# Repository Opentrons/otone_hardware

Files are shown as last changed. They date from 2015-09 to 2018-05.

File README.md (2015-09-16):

# OT.One Hardware

This repository contains all 3D models and Bill of Materials necessary for independent construction of the opensource OT.One lab automation platform.

If you require more information or assets to complete your construction, please don't hesitate to create an issue in this repository.

This hardware is meant to operate in conjunction with an integrated [software stack](https://github.com/OpenTrons/otone_central), designed for the Raspberry Pi.

## Open Parts List

### Lasercut

* 1001 - [Baseplate](models/1001_A_Baseplate.dxf) x1 (6061 Aluminum, Anodized, 3mm)
* 1002 - [Motor Mount Plate](models/1002_Motor_Mount_Plate.dxf) x5 (6061 Aluminum, Anodized, 3mm)
* 1003 - Computer Mount Set x1 (Acrylic, 3mm)
* 1004 - [Home Switch Mount Set](models/1004_Home_Switch_Mount_Set.dxf) x1 (Acrylic, 3mm)
* 1005 - [Z Rail Spacer](models/1005_Z_Rail_Spacer.dxf) x1 (Acrylic, 5mm)
* 1006 - [Pipette Rail Mount](models/1006_Pipette_Rail_Mount.dxf) x1 (Acrylic, 5mm)
* 1007 - [A Motor Mount Set](models/1007_A_Motor Mount_Set.dxf) x1 (Acrylic, 8mm)
* 1008 - [Z Motor Mount](models/1008_Z_Motor_Mount.dxf) x1 (Acrylic, 8mm)
* 1009 - [Z Motor Lock](models/1009_Z_Motor_Lock.dxf) x1 (Acrylic, 8mm)
* 1010 - [Cable Rail Bracket](models/1010_Cable_Rail_Bracket_A.stl) x2 (Acrylic, 8mm)
* 1011 - [Baseplate Rails](models/1011_Baseplate_Rails.dxf) x1 (Acrylic, 3mm, 8mm)

### 3D Printed (PLA)

* 1100 - [Belt Clip](models/1100_F_Belt_Clip.stl) x3
* 1101 - Pipette Holder x1
* 1102 - [Pipette Stopper](models/1102_Pipette_Stopper.stl) x1
* 1106 - Z Motor Mount x1
* 1107 - Z Motor Lock x1
* 1150 - Tip Clip x1
* 1151 - [Z Switch Block](models/1151_Z_Switch_F1.stl) x1
* 1152 - Pipette Rail Mount x1

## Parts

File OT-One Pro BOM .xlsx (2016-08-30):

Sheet: Sheet1
Section | Type | Part Name | Quantity | Drawing | Description
Base/Deck Components | Deck/Base Set | Corner Angle L-Bracket | 4
 |  | Lrg. M5 Inserts | 8
 |  | M5 x 12 Screws | 8
 |  | Base Plate with 8 rack Holders | 1
 |  | M4 x 10 Screws | 4
 |  | M4 Lrg. Spin Inserts | 4
 |  | 1515-S T-slot Aluminum Extrusion Bar | 4 |  | 550mm long
 |  | L-Shape interior Bracket | 8
 |  | M6 x 8 | 16
 |  | 25-2527 T-slot Extrusion Bar | 4 |  | 600 mm long
Y - Axis Components | Y- Rail Set (2) | 20-2040 T-slot Extrusion Bar | 2
 |  | Aluminum Plate | 2
 |  | Motor | 2 |  | Attached to plate with 4 screws
 |  | Wheels | 8 |  | each comes with nut and M4 screw attached to plate
 |  | Corner Bracket | 8 |  | Each needs LG M5 Insert,SM M5 Insert, M5 x 12, M5 x 8
 |  | M5 Screws | 16 |  | M5 x 12 (8), M5 x 8 (4), M5 x 16 (4)
 |  | Lrg. M5 Inserts | 8
 |  | Sm. M5 Inserts | 8
 |  | Motor Belt | 2
 |  | Belt Holder | 4 |  | 3D Printed
 |  | Belt Driver | 2 |  | Attached to each motor
X - Axis Components | X- Rail Set | 20-2040 T-slot Extrusion Bar | 1
 |  | Motor | 1 |  | Attached to plate with 4 screws
 |  | Wheels | 4 |  | Each comes with nut and M4 attached to plate
 |  | Motor Belt | 1
 |  | Belt Holder | 2 |  | 3D printed
 |  | Belt Driver | 1 |  | Attached to motor
 |  | Aluminum Plate | 2
 |  | Corner Angle L-Bracket | 4 |  | Each needs M5 x 8, M5 x 16
 |  | M5 Screws | 12 |  | M5 x 16 (6), M5 x 8 (4), M5 (2)
 |  | SM M5 Inserts | 6
 |  | Brass Spacer | 1
 |  | M5 Nut | 4
Z - Axis Components
 |  | Motor | 3 |  | With 4 screws holding
 |  | 6 3/4" Aluminum Bar | 2 |  | 6 3/4"
 |  | 20-2040 T-slot Extrusion Bar | 1 |  | 11 5/8" long
 |  | Plexi-Glass Plate | 1
 |  | M5 x 12 | 4 |  | Behind Plexi + Metal
 |  | M5 x 10 | 4 |  | Behind plexi
 |  | SM M5 Inserts | 12
 |  | Aluminum Plate | 1
 |  | M4 X 8 Countersunk | 4
 |  | Sq. M4 Inserts | 4
 |  | Plexi-Plunger Set | 2 |  | 3D printed
 |  | L-Shape Stoppers | 2
 |  | M4 x 8 or 10 | 6
 |  | Sq. M4 Inserts | 6
 |  | Wheels | 4 |  | each comes with nut and M4 attached to plate
 |  | 3D Printed Z Holder
 |  | M5 x 16 | 2
 |  | Z Motor Screw | 1
 |  | Z Nut for Motor Screw Holder | 1 |  | Already Attached to Z Motor Screw Holder with 4 small screws.
 |  | 25-2525 T-slot Extrusion Bar | 2 |  | 5" long
 |  | Z Motor Screw Holder | 1
 |  | M5 X >12 | 4
 |  | M5 x 25 (Plunger) | 2
 |  | M5 Lrg spins | 4
Pre-Wire Set Up
 |  | 3D Print X-rail Holder | 2
 |  | M5 x 12 | 10
 |  | SM M5 Spin Inserts | 10
 |  | 25-2525 T-slot Extrusion Bar | 1 |  | X-Rail support for cable track
 |  | Corner Angle L-Bracket | 3
 |  | M5 x 10 | 6
 |  | SM M5 Insert | 3
 |  | M5 Nut | 1
 |  | 25-2525 T-slot Extrusion Bar | 1 |  | Motor Controller support for cable track/hose carrier
 |  | M5 Ball Inserts | 2
 |  | M3 Insert | 2
 |  | M3 Screw | 2
 |  | Cable Track/Hose Carrier | 2
 |  | Camera Mount Holder | 1 | 3D Printed
 |  | M4 x 10 | 4
 |  | SM M4 Insert | 4
 |  | Z Home Switch | 1
 |  | X & Y Home Switch | 2
 |  | M5 x 8 | 4
 |  | M5 Inserts | 4
 |  | A & B Home Switch | 2 | 3D Printed
Wiring |  | Bumpers | 3
 |  | Home Switches | 5
 |  | Motor Cable Spilter | 1
 |  | Short Home Switch Cable | 2
 |  | Long Home Switch Cables | 3
 |  | Motor Cables | 5
 |  | Camera Cable | 1
Motor-Controller Case
 |  | Rasberry Pi | 1
 |  | Smoothie Board | 1
 |  | Aluminum Motor Controller Box | 1
 |  | M5 x 8 | 2
 |  | SM M5 Spin Inserts | 2
 |  | M4 x 8 | 4
 |  | Aluminum Back Cover | 1
 |  | M4 Countersink Screws | 4
 |  | Plastic Nuts | 8
 |  | Plastic Screws (?) | 8
 |  | Plastic Standoff 20mm | 4 |  | For R.Pi
Final/ Locks |  | Plastic Standoff 10 or 8 mm | 4 |  | For Smoothie-Board
 |  | J - Aluminum Extruded Bar | 3
 |  | 3-Way Connection Angle for profile 40 series | 4
 |  | M8 x 14 | 10
 |  | Plastic Corner Covers | 4

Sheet: Sheet2
Part Type | Part Name | Drawing/Image | Overall Quantity | Description
Screws | M5 X 8
 | M5 X 10
 | M5 X 12
 | M5 X 16
 | M5 X 25
 | M4 X 8
 | M4 X 10
 | M4 CounterSunk
 | M3
 | M6 X 8
 | Plastic Screws
Inserts | LG M5 Insert
 | SM M5 Insert
 | SM M5 Spin Insert
 | M5 Ball Inserts

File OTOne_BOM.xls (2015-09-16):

OpenTrons OT.One BOM
Category | Part Number | Part Name | Quantity | Description
Lasercut
 | 1001 | Baseplate | 1 | 6061 Aluminum, Anodized, 3mm
 | 1002 | Motor Mount Plate | 5 | 6061 Aluminum, Anodized, 3mm
 | 1003 | Computer Mount Set | 1 set | Acrylic, 3mm
 | 1004 | Home Switch Mount Set | 1 set | Acrylic, 3mm
 | 1005 | Z Rail Spacer | 1 | Acrylic, 5mm
 | 1006 | Pipette Rail Mount | 1 | Acrylic, 5mm
 | 1007 | A Motor Mount Set | 1 set | Acrylic, 8mm
 | 1008 | Z Motor Mount | 1 | Acrylic, 8mm
 | 1009 | Z Motor Lock | 1 | Acrylic, 8mm
 | 1010 | Cable Rail Bracket | 2 | Acrylic, 8mm
 | 1011 | Baseplate Rails | 1 set | Acrylic, 3mm, 8mm
3D Print
 | 1100 | Belt Clip | 3 sets | PLA
 | 1101 | Pipette Holder | 1 | PLA
 | 1102 | Pipette Stopper | 1 | PLA
 | 1106 | Z Motor Mount | 1 | PLA
 | 1107 | Z Motor Lock | 1 | PLA
 | 1150 | Tip Clip | 1 | PLA
 | 1151 | Z Switch Block | 1 | PLA
 | 1152 | Pipette Rail Mount | 1 | PLA
Motors and Wheels
 | 1200 | Nema 17 Stepper Motor | 3 | Motor used for Y1, Y2, and X rails
 | 1201 | Nema 17 Stepper Motor | 1 | Motor used for Z Axis, 300mm Captive Lead screw
 | 1202 | Nema 17 Stepper Motor | 1 | Motor used for A pipette, 100mm Captive Lead screw
 | 1203 | Pulley | 3 | MX5-20 pulley for Y1, Y2, and X motors
 | 1204 | Wheels | 16 | Delrin V-Profile Wheel Kit
 | 1205 | Belt | 3 | MX5-belt – 600mm
Electrical
 | 1300 | Homeswitch | 4 | Micro switch used for homing feedback
 | 1301 | Homeswitch Cable | 2 | 3 pin, 2m long for Z and A home switch
 | 1302 | Homeswitch Cable | 2 | 3 pin, 1 m long for X and Y home switch
 | 1303 | Motor Cable | 4 | 4 pin, 2m long for Y, X, Z, and A motors
 | 1304 | Y-Split Cable | 1 | 4pin splits into two sections for Y1, and Y2 motor. 41Cm long
 | 1305 | Power Supply | 1 | 12V, 5.0A
 | 1306 | Power Button | 1
 | 1307 | Power Supply Cord | 1
 | 1308 | Cable Chain | 2
 | 1309 | Aluminum Board Case | 1 | 145mm x 85mm x 200mm
Nuts and Bolts
 | 1400 | M8 Flathead Socket Cap Screw | 10 | 14mm
 | 1401 | M5 Buttonhead Socket Cap Screw | 4 | 35mm
 | 1402 | M5 Buttonhead Socket Cap Screw | 19 | 14mm
 | 1403 | M5 Buttonhead Socket Cap Screw | 14 | 12mm
 | 1404 | M5 Buttonhead Socket Cap Screw | 40 | 10mm
 | 1405 | M5 Buttonhead Socket Cap Screw | 15 | 8mm
 | 1406 | M4 Flathead Socket Cap Screw | 2 | 8mm
 | 1407 | M4 Buttonhead Socket Cap Screw | 6 | 10mm
 | 1408 | M4 Buttonhead Socket Cap Screw | 1 | 8mm
 | 1409 | M3 Sockethead Cap Screw | 5 | 12mm
 | 1410 | M3 Buttonhead Socket Cap Screw | 8 | 16mm
 | 1411 | M3 Buttonhead Socket Cap Screw | 24 | 12mm
 | 1412 | M3 Buttonhead Socket Cap Screw | 30 | 8mm
 | 1413 | M5 T-Slide Nut | 34 | 15mm x 15mm x 6mm
 | 1414 | M5 T-Slide Nut | 33 | 10mm x 10mm x 5mm
 | 1415 | M5 Locknut | 6
 | 1416 | M5 Elastic Nut Ball Nut | 4 | 13.5mm x 8.5mm x 4.5mm
 | 1417 | M4 Square Nut | 8
 | 1418 | M4 T-Slide Nut | 4 | 15mm x 15mm x 6mm
 | 1419 | M3 T-Slide Nut | 2 | 10mm x 10mm x 5mm
 | 1420 | M3 washer | 8
 | 1421 | M3 nut | 24
 | 1422 | M3 insert | 16 | 5mm height, press fit
 | 1423 | M5 Standoff | 1 | 30mm length, Both sides female
 | 1424 | M3 Standoff | 12 | 45mm length, 1 side male 1 side female
 | 1425 | M3 Standoff | 4 | 60mm length, 1 side male 1 side female
 | 1426 | M3 Standoff | 4 | 6mm, 1 side male 1 side female
 | 1427 | L Bracket | 27 | 30mm x 30mm x 20mm
 | 1428 | L Bracket | 2 | 20mm x 20mm x 20mm
 | 1429 | 3-Side Bracket | 4 | 30mm x 30mm x 30mm
 | 1430 | Pin | 4 | 3mm Diameter, 8mm Height
 | 1431 | Precision Rod | 3 | 5mm Diameter, 100mm height
 | 1432 | Spacer | 3 | 5mm diameter, 8mm height
 | 1433 | Phillips Self-Tap Screw | 4 | 16mm
Rails
 | 1500 | Frame – Base Rails | 4 | Aluminum Extrusion – J3030 – 30mm x 30mm x 550mm
 | 1501 | Frame – Top Rails | 3 | Aluminum Extrusion – JR3030 – 30mm x 30mm x 550mm
 | 1502 | Frame – Posts | 4 | Aluminum Extrusion – JR3030 – 30mm x 30mm x 600mm
 | 1503 | Frame – Cable Rail | 1 | Aluminum Extrusion – JA2020 – 20mm x 20mm x 540mm
 | 1504 | Frame – J Rail | 1 | Aluminum Extrusion – JA2020 – 20mm x 20mm x 550mm
 | 1505 | X and Y Linear Rail | 3 | Aluminum Extrusion – V-Profile – 20mm x 40mm x 550mm
 | 1506 | Z Linear Rail | 1 | Aluminum Extrusion – V-Profile – 20mm x 40mm x 330mm
 | 1507 | A Rail | 1 | Aluminum Extrusion – CJ2040-4 – 40mm x 20mm x 175mm
 | 1508 | Pipette Rail | 1 | Aluminum Extrusion – JA2020 – 20mm x 20mm x 125mm

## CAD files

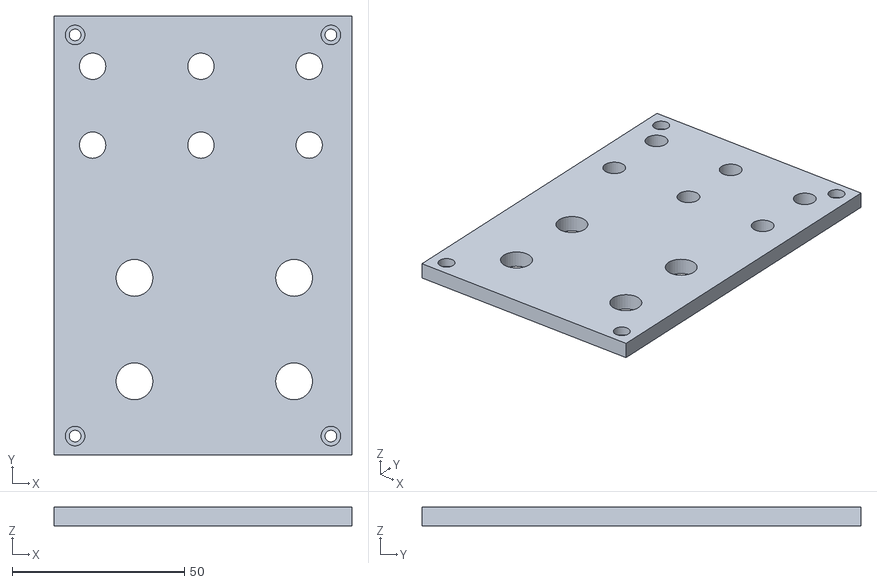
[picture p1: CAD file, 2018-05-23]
models/Tube rack BOTTOM.STL
86.5 x 127.5 x 5.50

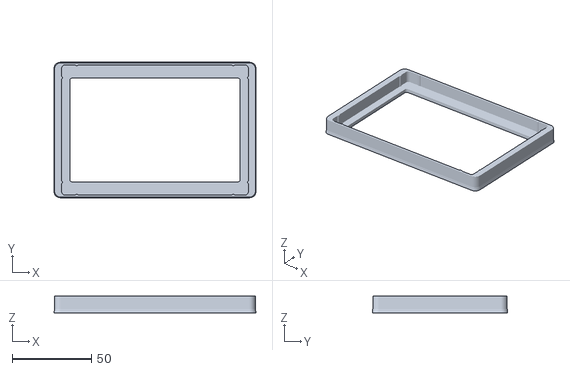
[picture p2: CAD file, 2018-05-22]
models/Life Gene 1250 uL tip rack adaptor.STL
127.7 x 85.7 x 10.5

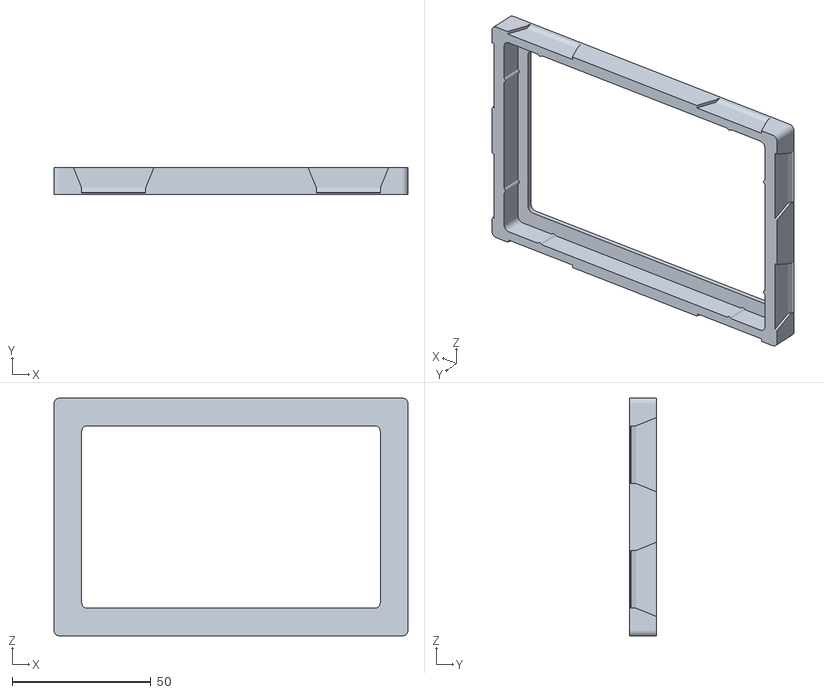
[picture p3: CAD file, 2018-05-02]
models/GEB 1000uL Tip Rack Adaptor.STL
127.7 x 9.75 x 85.8

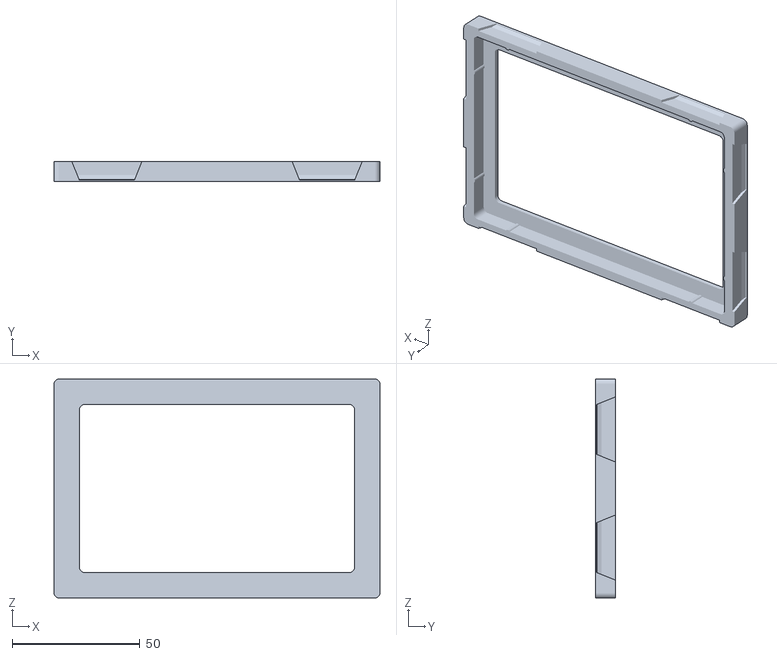
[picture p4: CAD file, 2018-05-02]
models/GEB 10uL Tip Rack Adaptor.STL
127.7 x 7.75 x 85.8

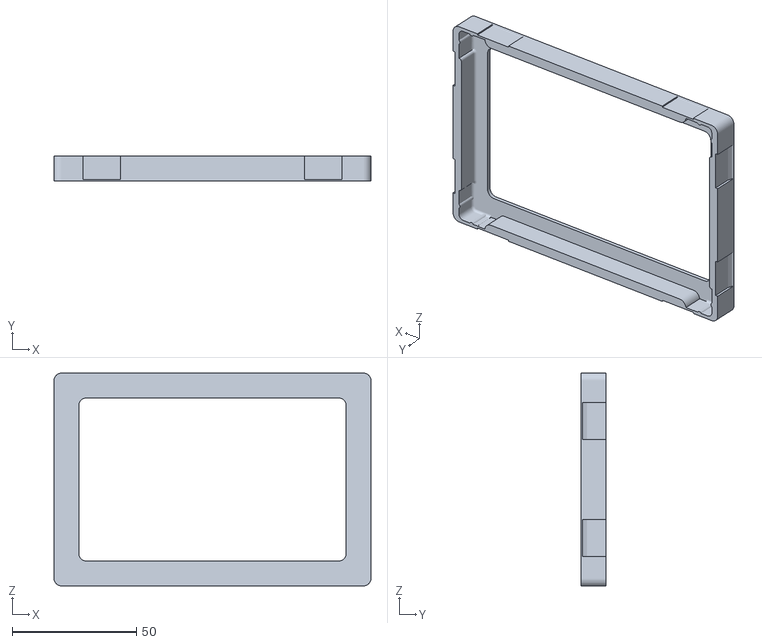
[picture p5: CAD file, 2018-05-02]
models/TipOne 10:200:300 uL Tip Rack Adaptor.STL
127.6 x 10.0 x 85.6

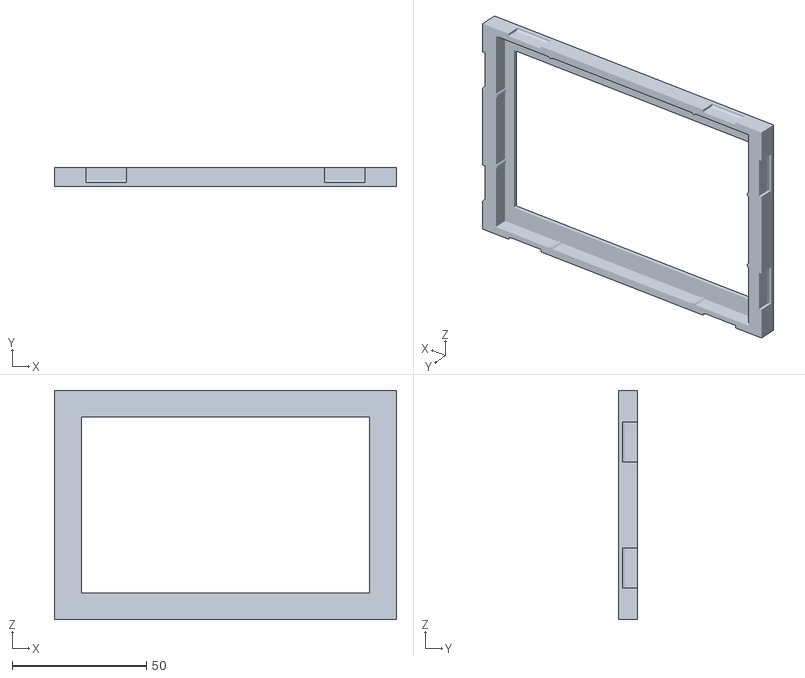
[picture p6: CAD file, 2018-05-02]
models/Rainin 200uL Tip Rack Adaptor .STL
127.5 x 7.00 x 85.5

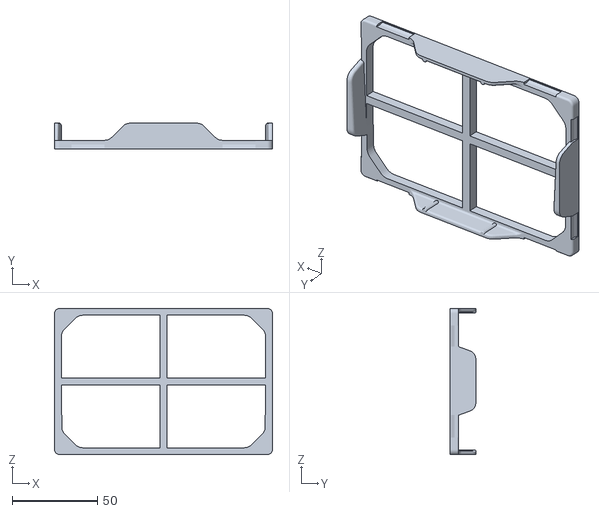
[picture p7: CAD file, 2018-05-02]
models/TipOne 1000uL Tip Rack Adaptor.STL
127.5 x 15.0 x 85.5

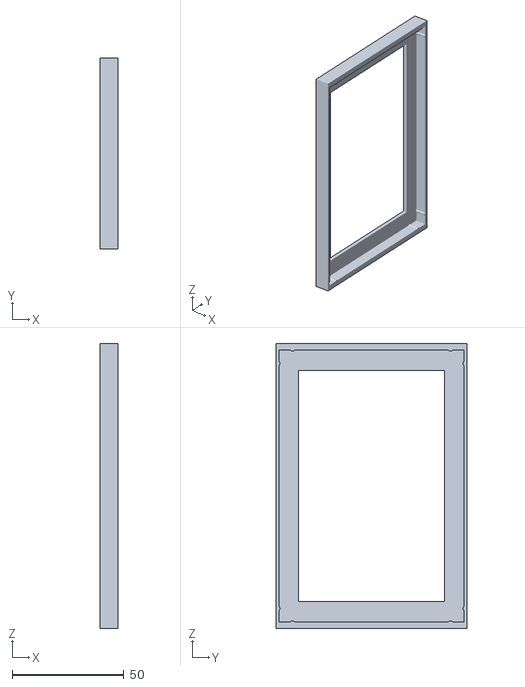
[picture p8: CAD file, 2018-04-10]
models/WVR 200uL Tip Rack Adaptor.STL
8.00 x 85.5 x 127.5

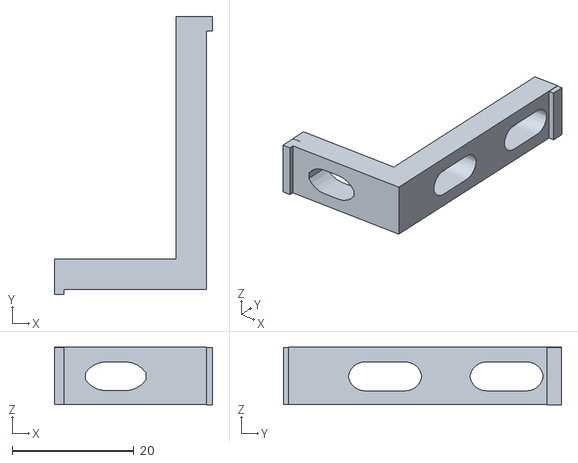
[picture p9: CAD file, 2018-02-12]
models/Locking L-bracket.STL
26.0 x 45.8 x 9.49

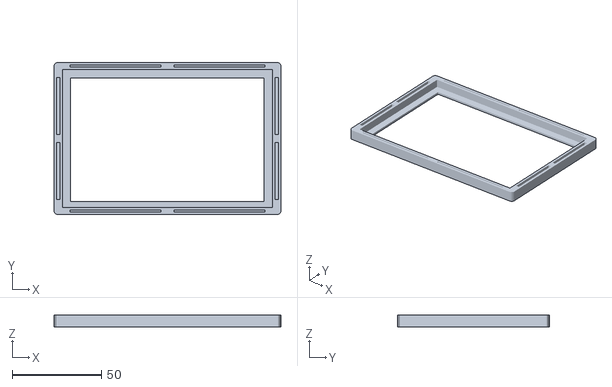
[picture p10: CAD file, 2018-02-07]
models/GEB Tip Rack.STL
127.1 x 85.1 x 6.50

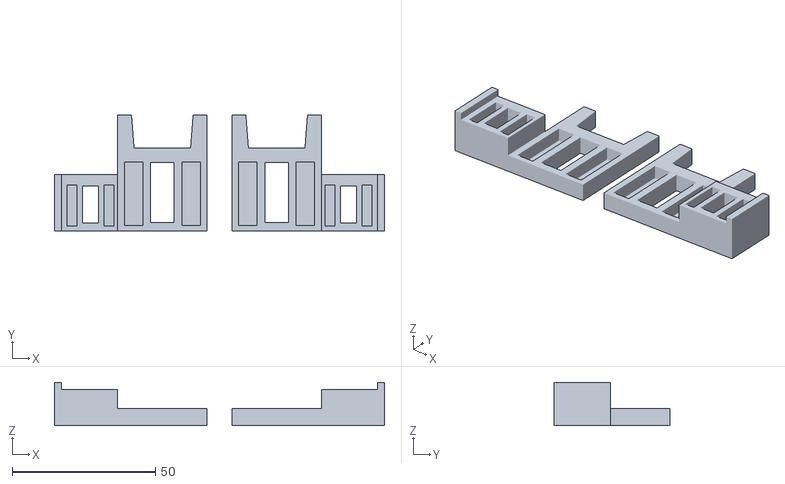
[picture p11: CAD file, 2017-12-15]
models/Rainin Multichannel pipette LTS.stl
115.1 x 40.4 x 15.0

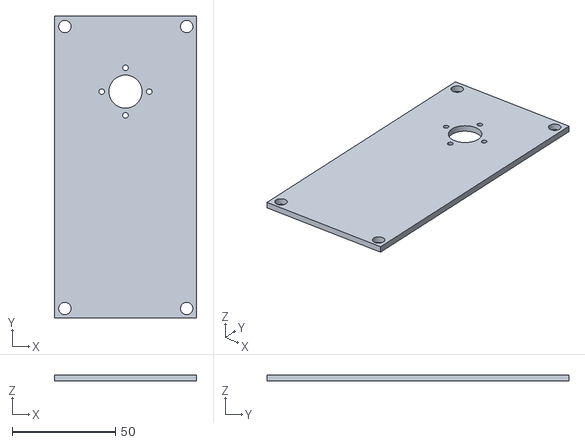
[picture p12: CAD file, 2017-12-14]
models/Hood OTMC Back Plate (Hub).stl
68.8 x 146.0 x 3.00

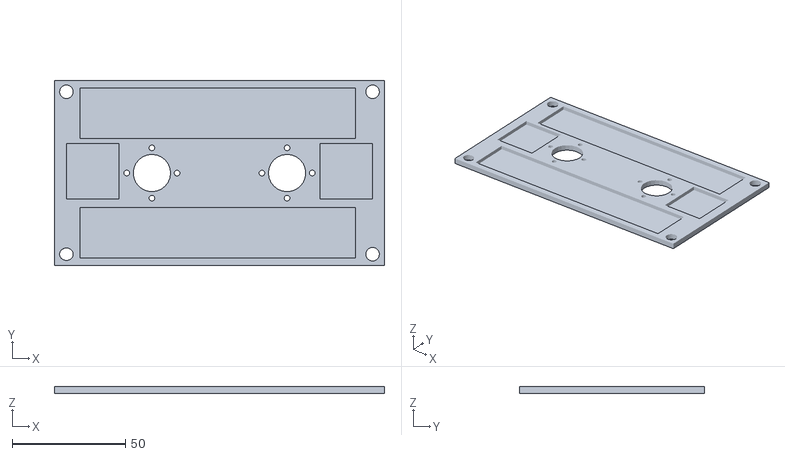
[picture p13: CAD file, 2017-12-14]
models/Pro OTMC Back Plate (Hub).STL
146.0 x 81.9 x 3.00

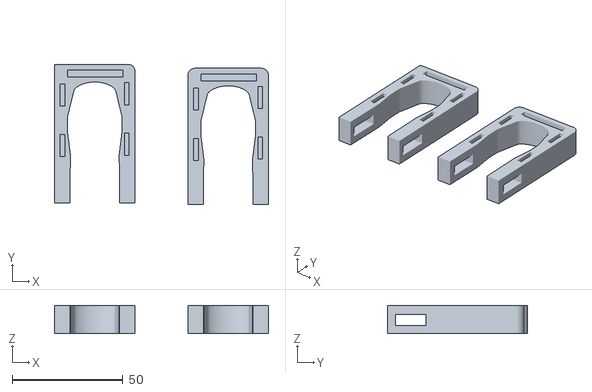
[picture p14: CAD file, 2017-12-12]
models/Rainin Pipette Clamps.STL
96.8 x 63.5 x 12.7

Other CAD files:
models/Hood Camera Mount.STL
models/Rainin Tip Rack Adaptor.stl
models/OT1 Case (Right Side).DXF
models/OT1 Case (rear).DXF
models/0.75mL tube TOP rack.stl
models/100 - Y-home switch.stl
models/1001_A_Baseplate.dxf
models/1002_Motor_Mount_Plate.dxf
models/1004_Home_Switch_Mount_Set.dxf
models/1005_Z_Rail_Spacer.dxf
models/1006_Pipette_Rail_Mount.dxf
models/1007_A_Motor Mount_Set.dxf
models/1008_Z_Motor_Mount.dxf
models/1009_Z_Motor_Lock.dxf
models/1010_Cable_Rail_Bracket_A.stl
models/1011_Baseplate_Rails.dxf
models/1012_Camera_Mount.dxf
models/1013_Etips_Rack_Top.dxf
models/1014_Etips_Rack_Bottom.dxf
models/1100_F_Belt_Clip.stl
models/1102_Pipette_Stopper.stl
models/1151_Z_Switch_F1.stl
models/132_camera_D.stl
models/15-50mL tube TOP rack.stl
models/2mL tube TOP rack.stl
models/498_C.stl
models/Accupet Pipette Clamp.STL
models/BioHit:Sartorius pipette clamps.STL
models/Camera Mount.STL
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

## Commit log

2015-09-16 AutoCAD files.
    [1001_A_Baseplate.dxf, 1002_Motor_Mount Plate.dxf, 1004_Home_Switch Mount_Set.dxf, 1005_Z_Rail Spacer.dxf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]
2015-09-16 Moved models to their own directory.
    [1001_A_Baseplate.dxf, 1002_Motor_Mount Plate.dxf, 1004_Home_Switch Mount_Set.dxf, 1005_Z_Rail Spacer.dxf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]
2015-09-16 Model filename cleanup.
    [132_camera_D.stl]
2015-09-16 Model name cleanup.
    [499_Z_switch_F1.stl]
2015-09-16 Bill of Materials.
    [OTOne_BOM.xls]
2015-09-16 Excel file for BOM now more compatible with third-party apps.
    [OTOne_BOM.xls]
2015-09-16 Spacing fix for filenames.
    [1004_Home_Switch_Mount_Set.dxf, 1008_Z_Motor_Mount.dxf, 1009_Z_Motor_Lock.dxf]
2015-09-16 Moving some files around.
    [1010_Cable_Rail_Bracket_A.stl, 1100_F_Belt_Clip.stl, 1151_Z_Switch_F1.stl]
2016-08-30 add OT-One Pro BOM.xlsx
    [OT-One Pro BOM .xlsx]
